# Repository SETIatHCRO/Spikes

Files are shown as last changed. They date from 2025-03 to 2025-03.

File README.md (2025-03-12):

## SPIKES - Spectrum Plotter and Interface Kit for EMI Scanning

SPIKES is a test setup to capture the emission profiles of potential RFI emitters at the Hat Creek Radio Observatory. 

The setup consists of a spectrum analyzer, a computer running the SPIKES application, an antenna and amplification system. 

The system is located in Lab 2 at HCRO, in this tutorial only local operation is covered. For more details on remote operation please refer to the documentation.

Measurement data should always be updated using git push to this repository (see Git_Push_Guide in the Documentation).

### Running the Application
To start the SPIKES application, log in to the Sonata account, navigate to the lower left side of the screen and click on the `SPIKES` icon:

SPIKES on Desktop

Or for the computationally adept run the following command in your terminal:

```bash
spikes
```

### Configuration

You can create a configuration file for the desired measurement or reuse an existing one. 

To access the configuration files, click on the `Configuration` icon on the lower left side of the screen:

Configuration Button

Again, for the experienced (or remote) user, the configuration files can be accessed directly from the terminal:

```bash
~/SPIKES/Configuration
```

Each configuration file contains the parameters to be sent to the spectrum analyzer, the parameters are loaded into the application and sent to the spectrum analyzer when the configuration is selected from the dropdown menu. 

If you edit or create a new configuration file, select RELOAD from the dropdown menu to update the current configuration files.

Note: there are two main modes of operation, `FAST` and `HIGH-RES`.

#### Example configuration (fast_track.yml):

FAST mode will perform a Max Hold measurement, this mode is useful to capture high-amplitude non-continous emissions like Wifi or Cellular.

In this example the spectrum analyzer will sweep from 300 MHz to 10 GHz with a resolution bandwidth of 500 kHz and a video bandwidth of 500 kHz. The attenuation is set to 10 dB to avoid damage to the spectrum analyzer (a strong signal is expected). The display will refresh every second and the integration time is set to 5 seconds. The total number of traces is set to 5.

This will result in a total measurement time of 25 seconds.

In this example the sweep time would be 45 milliseconds which will be displayed as soon as the configuration is loaded into the spectrum analyzer. This means that each trace will contain the max hold values of 111 sweeps. ($\frac{5 s}{0.045 s}$ = 111.1 = 111 sweeps) 

```yaml
sweep_points:       1001    # number of points
start_freq:         300e6   # Hz
stop_freq:          10e9    # Hz
res_bw:             500e3   # Hz
vid_bw:             500e3   # Hz
attenuation:        10      # dB
mode:               FAST    # Mode of operation: HIGH-RES or FAST
# mode specific parameters
display_refresh:    1       # seconds (int or float)
integration_time:   5       # seconds (integer)
total_traces:       5       # integer or "cont" for continuous operation
```

#### Example configuration (slow_coach.yml):

HIGH-RES mode will perform a clear sweep of the spectrum for every trace, this mode is useful to capture low-amplitude continuous emissions like clock signals or harmonics.

In this example the spectrum analyzer will sweep from 300 MHz to 6 GHz with a resolution bandwidth of 5 kHz and a video bandwidth of 5 kHz. The attenuation is set to 0 dB (a faint signal will be measured). The mode is set to HIGH-RES and the number of traces is set to 2.

The sweep time will be 264.233 seconds, which will result in a total measurement time of 9 minutes.

```yaml
sweep_points:   1001        # number of points
start_freq:     300e6       # Hz
stop_freq:      6e9         # Hz
res_bw:         5e3         # Hz
vid_bw:         5e3         # Hz
attenuation:    0           # dB 
mode:           HIGH-RES    # Mode of operation: HIGH-RES or FAST
# mode specific parameters
num_aver:       2           # number of traces
```

### Measurement Process
1. Select a configuration from the dropdown menu.
2. Click the Start button to begin the measurement.
3. The progress bar will update to show the measurement progress.
4. The Stop button can be used to stop the measurement at completion of the current trace.
5. The Save button will open a dialog to save the data to a file.

Please note that stopping a measurement will always wait on completion of the current trace, as the limitations of GPIB communications do not allow to reset the specturm analyzer during the sweep. 

It is still possible however to stop the measurement manually by pressing the ESC button on the spectrum analyzer to exit remote operation and setting the resolution bandwith very high to end the current measurement quickly (which will reestablish GPIB responsiveness of the spectrum analyzer). This will of course result in no data being captured.

### Measurement Data

To access the measurement data, click on the `Measurements` icon on the lower left side of the screen:

Measurements Button

Or for the terminal savvy:

```bash
~/SPIKES/Measurements
```

The folder structure is automatically created and organized as follows:

```
Measurements
├── date[YYYY-MM-DD]
│   ├── time[HHhMM]-[config_name]
│   │   ├── data
│   │   │   ├── config file[config_name].yml
│   │   │   └── trace_n.csv
|   |   ├── imgs_legend
|   |   |   ├── combined_trace.png
|   |   |   └── trace_n.png
|   |   └── imgs_nolegend
|   |       ├── combined_trace.png
|   |       └── trace_n.png
```

for example:

`Measurements/2025-01-01/12h00-fast_track/data/trace_1.csv`

### Setup Schematic

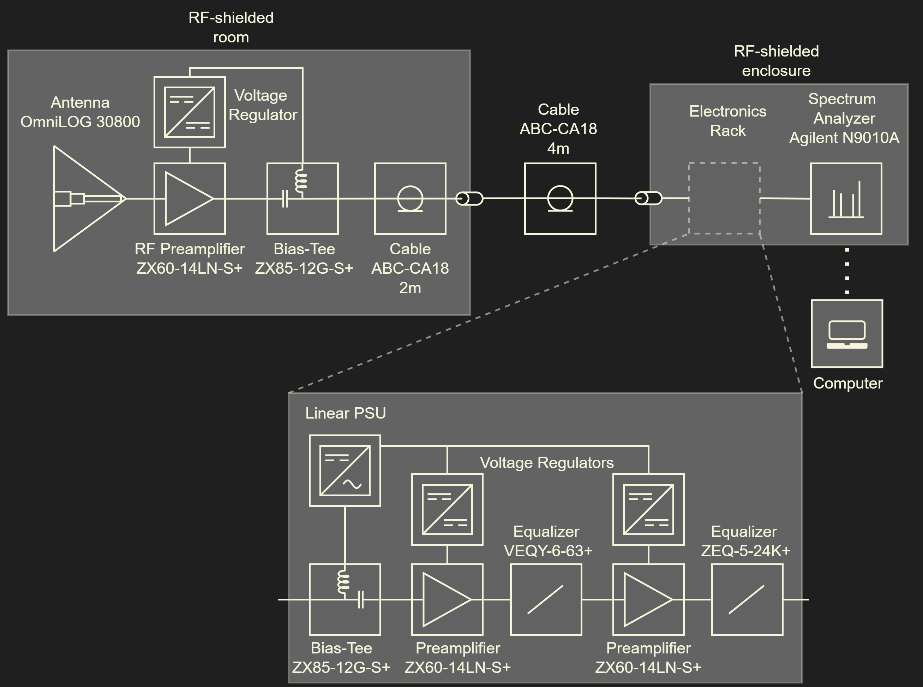
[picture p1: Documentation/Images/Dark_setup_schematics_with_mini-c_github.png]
Setup Schematic


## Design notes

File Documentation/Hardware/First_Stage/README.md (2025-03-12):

### First-Stage Amplifier Enclosure
This Enclosure is designed to house first-stage Mini-Circuits ZX60-14LN-S+ Amplifier, Bias-Tee and a Linear Voltage Regulator.

The Enclosure is designed to be mounted on a standard tripod mount, and has a 1/4" UNC thread on the bottom and back.

The Amplifier is powered via a 6V Linear Voltage Regulator, which has to be supplied by a 12V bias in the outgoing coaxial cable.

The Device was designed in Autodesk Inventor 2025, all necessary design files can be found in this directory.

The Enclosure is designed to be 3D printed, the step files in the directory are ready to print (however the current enclosures where printed with sla and sls processes and fdm is not yet tested).

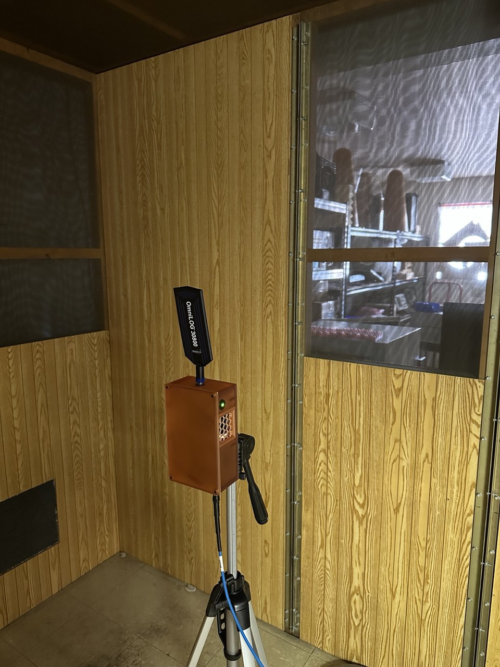
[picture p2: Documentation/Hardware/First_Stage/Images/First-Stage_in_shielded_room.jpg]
In Shielded Room

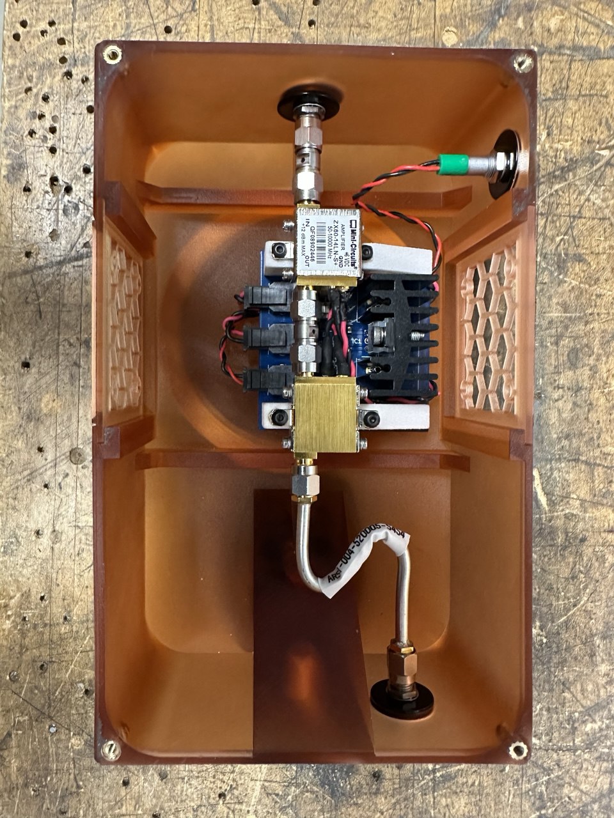
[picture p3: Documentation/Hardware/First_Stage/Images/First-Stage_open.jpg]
First Stage Open


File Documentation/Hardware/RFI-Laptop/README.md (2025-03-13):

### RFI-Laptop

Info about the dedicated Laptop for Spikes in Lab 2

#### General

  OS: Ubuntu 24.04 LTS

  Hostname: RFI-Laptop1.hcro.org

  Static-IP: 192.182.123.54

  BIOS-Settings: `Security -> I/O Port Access` Bluetooth: OFF, WiFi: OFF

#### Hardware

  Model: Lenovo ThinkPad E14 Gen 5 - 21JSS0Y500

  Processor: AMD Ryzen 7 7730U @ 2.00 GHz 1 Processor, 8 Cores, 16 Threads 

  Ram: 14.83 GB DDR4 SDRAM

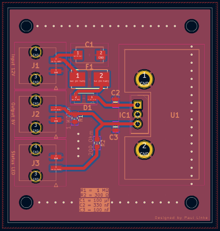
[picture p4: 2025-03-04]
Documentation/Hardware/Linear_Voltage_Regulator_6V/Images/Linear_Voltage_Regulator_Footprint.png

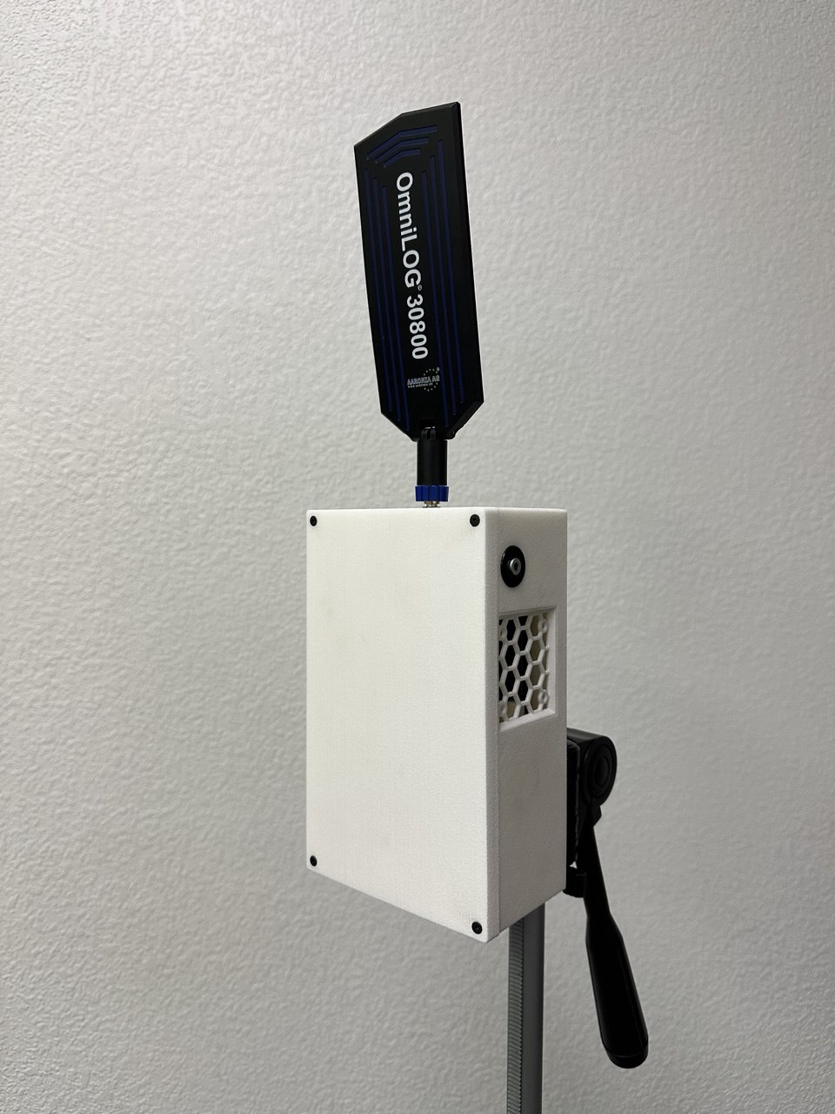
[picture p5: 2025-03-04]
Documentation/Hardware/First_Stage/Images/First-Stage_Nylon_Antenna.jpg

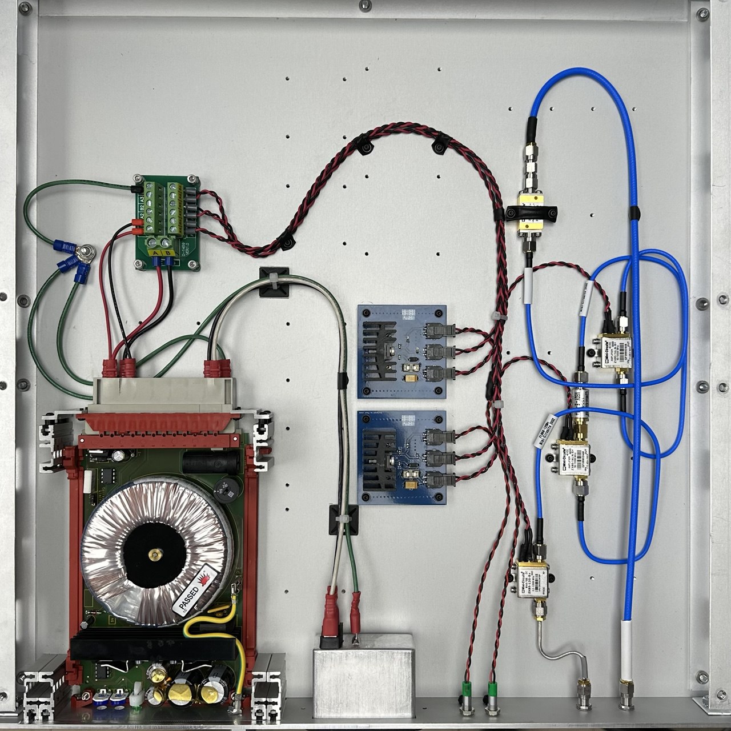
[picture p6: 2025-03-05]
Documentation/Hardware/Second_Stage/Images/Second_Stage_Top.jpg

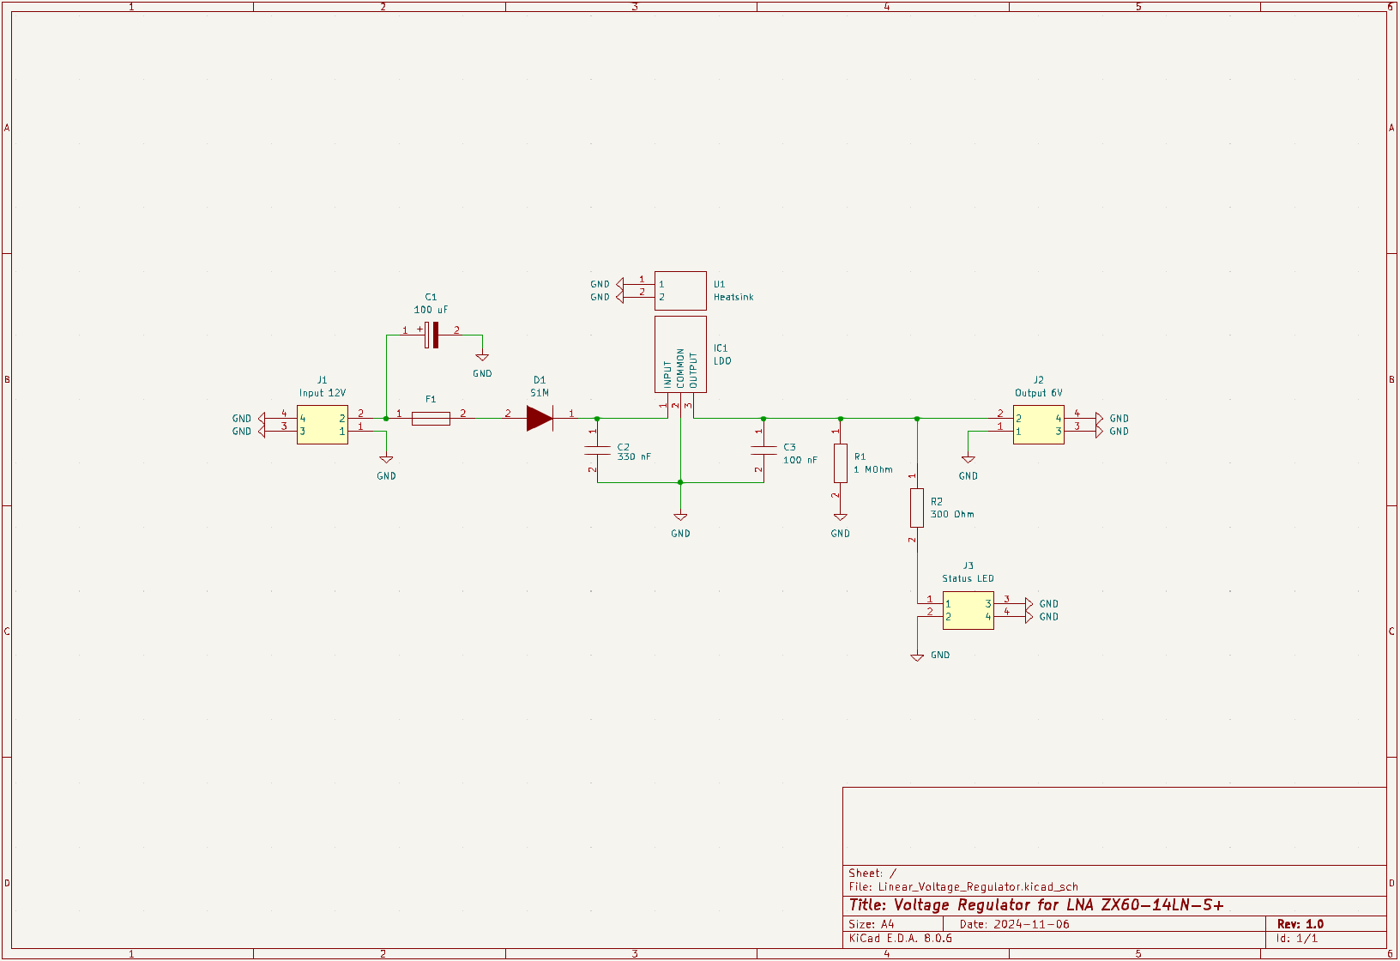
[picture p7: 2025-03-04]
Documentation/Hardware/Linear_Voltage_Regulator_6V/Images/Linear_Voltage_Regulator_Schematic.png

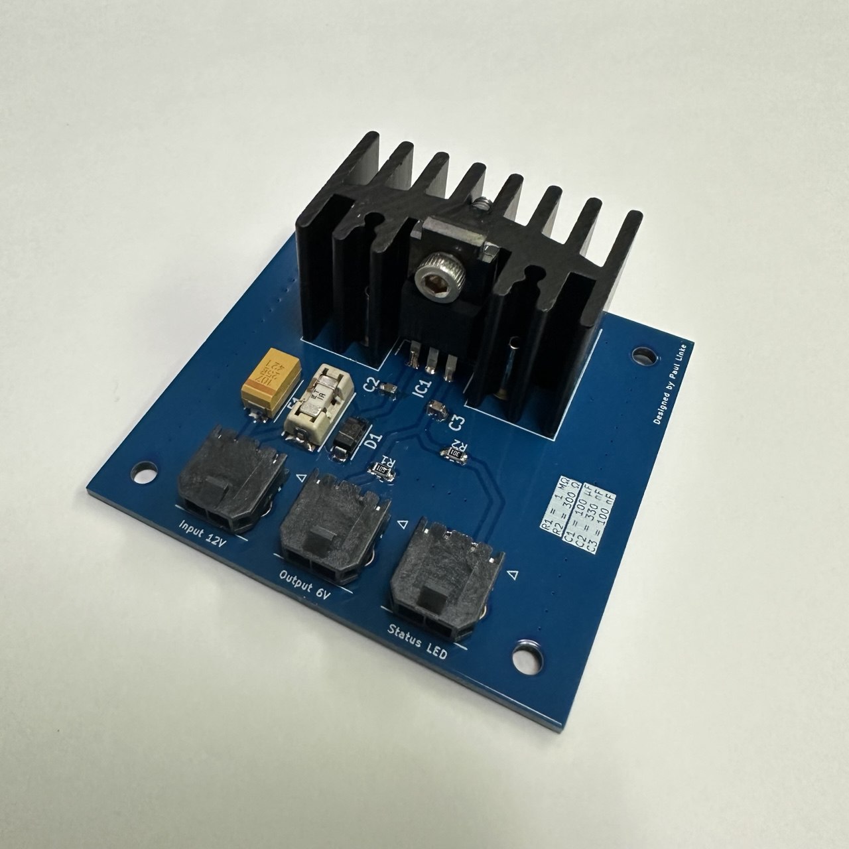
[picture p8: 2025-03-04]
Documentation/Hardware/Linear_Voltage_Regulator_6V/Images/Linear_Voltage_Regulator_real.png

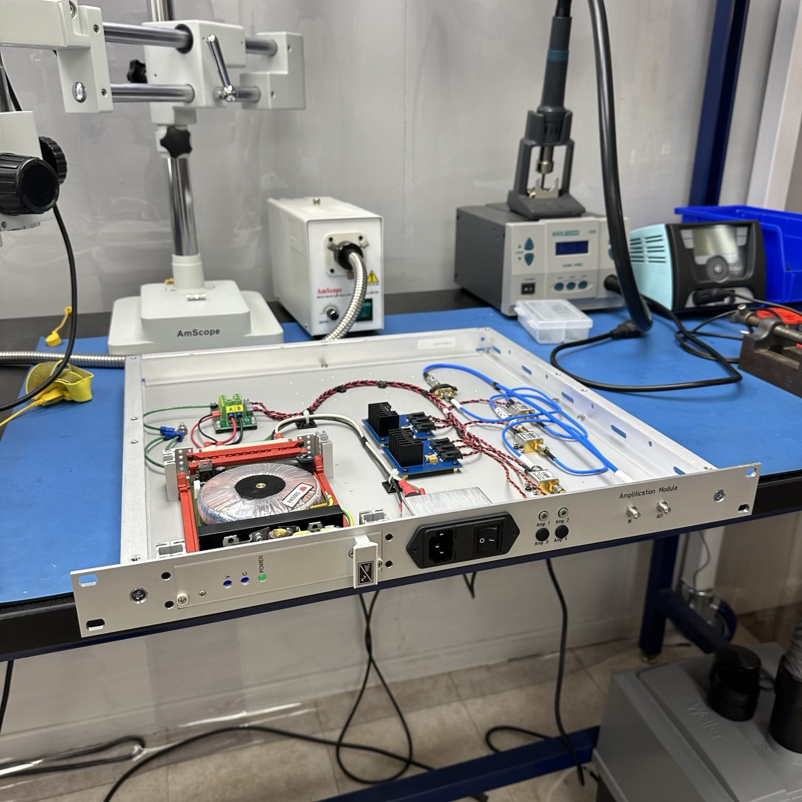
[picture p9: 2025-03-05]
Documentation/Hardware/Second_Stage/Images/Second_Stage_Front.jpg

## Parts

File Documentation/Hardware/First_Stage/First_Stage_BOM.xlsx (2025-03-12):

Sourcing List for SPIKES First Stage
QTY | Type | Name | Formfactor/Package | Manufacturer | Mfr. # | Link Vendor | Datasheet | Vendor
1 | Amplifier | ZX60-14LN-S+ | Mini-Circuits - GC957 | Mini-Circuits | ZX60-14LN-S+ | https://www.minicircuits.com/WebStore/dashboard.html?model=ZX60-14LN-S%2B | https://www.minicircuits.com/pdfs/ZX60-14LN-S+.pdf | Mini-Circuits
1 | Bias-Tee | ZX85-12G-S+ | Mini-Circuits - GC957 | Mini-Circuits | ZX85-12G-S+ | https://www.minicircuits.com/WebStore/dashboard.html?model=ZX85-12G-S%2B | https://www.minicircuits.com/pdfs/ZX85-12G-S+.pdf | Mini-Circuits
2 | SMA-Male2Male | SM-SM50+ | Mini-Circuits - DJ951 | Mini-Circuits | SM-SM50+ | https://www.minicircuits.com/WebStore/dashboard.html?model=SM-SM50%2B | https://www.minicircuits.com/pdfs/SM-SM50+.pdf | Mini-Circuits
2 | SMA-Passthrough | SM-SF50+ | Mini-Circuits - DJ952 | Mini-Circuits | SM-SF50+ | https://www.minicircuits.com/WebStore/dashboard.html?model=SF-SF50%2B | https://www.minicircuits.com/pdfs/SF-SF50+.pdf | Mini-Circuits
1 | LED | LED Green Panelmount | Panelmount, 6mm hole | Apem | Q6F3GXXG02E | https://www.mouser.com/ProductDetail/Apem/Q6F3GXXG02E?qs=4pzlT8jjbhczJGL6%2Fke6ug%3D%3D (https://www.minicircuits.com/WebStore/dashboard.html?model=ZX85-12G-S%2B) | https://www.mouser.com/datasheet/2/26/indicators_serie_Q6_-3359460.pdf | Mouser
1 | SMA-Male2Male | SMA-Cable 80mm | SMA-SMA Formable | Pasternak | PE3867LF-9CM | https://www.pasternack.com/showProduct.aspx?ProductID= | https://www.pasternack.com/images/ProductPDF/PE3867LF.pdf | Pasternak
1 | Threaded Insert | Ruthex - RX-M2.5x5.7 - 70 pcs | M2.5x5.7 | Ruthex | GE-M25x57-001 | https://www.amazon.com/ruthex-Threaded-Insert-Pieces-Ultrasound/dp/B088QJDPKK/ref=sr_1_3?sr=8-3 | https://www.ruthex.de/en/collections/gewindeeinsatze/products/ruthex-gewindeeinsatz-m2-5-70-stuck-rx-m2-5x5-7-messing-gewindebuchsen | Amazon
1 | Threaded Insert | Ruthex - RX-1/4" 20x12.7 - 20 pcs | 1/4"x12.7 | Ruthex | GE-1/4x127-001 | https://www.amazon.com/ruthex-Thread-Insert-20x12-7-Ultrasound/dp/B09MTS6ZZQ/ref=sr_1_3?sr=8-3 | https://www.ruthex.de/en/collections/gewindeeinsatze/products/ruthex-gewindeeinsatz-1-4-kameragewinde-20-stuck-rx-1-4-20x12-7-messing-gewindebuchsen-fur-3d-dr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 | Amazon
1 | Washers | M6 Washers | M6x1.3x17.7 | kvohlum | - | https://www.amazon.com/M6-Stainless-Washers-17-7mm-Diameter/dp/B0CX5GR7KG?cv_ct_cx=m7%2Bwasher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 | none | Amazon
1 | Standoffs | M2.5 Standoff Assortment Brass | M2.5 assortment | helifouner | - | https://www.amazon.com/HELIFOUNER-Standoffs-Assortment-Threaded-Motherboard/dp/B0B7SNCFF1?s=industrial&sp_csd=d2lkZ2V0TmFtZT1zcF9hdGY | none | Amazon
1 | Screws | M2.5 Screw Assortment Steel Countersunk | M2.5 assortment | Kindroufly | - | https://www.amazon.com/Kindroufly-Pieces-Countersunk-Washers-Assortment/dp/B0BLCG712G | none | Amazon
1 | Screws | M2.5 Screw Assortment Steel Button Head | M2.5 assortment | Kindroufly | - | https://www.amazon.com/Kindroufly-Pieces-Countersunk-Washers-Assortment/dp/B0BLCG5VS6 | none | Amazon
1 | 3d Print | First Stage Bottom |  | HCRO | First_Stage_BoxBottom.ipt |  |  | PCBWay
1 | 3d Print | First Stage Top |  | HCRO | First_Stage_BoxTop.ipt |  |  | PCBWay
1 | 3d Print | Voltage Regulator Bracket Left |  | HCRO | PCB-LNA.ipt |  |  | PCBWay
1 | 3d Print | Voltage Regulator Bracket Right |  | HCRO | PCB-LNA_MIR.ipt |  |  | PCBWay
2 | 3d Print | Hex-Grill |  | HCRO | First_Stage_HexGrill.ipt |  |  | PCBWay

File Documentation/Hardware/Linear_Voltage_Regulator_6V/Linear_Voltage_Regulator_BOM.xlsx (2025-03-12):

Sourcing List for 10x LDO_PSU PCB
QTY | Unit | Type | Name | Formfactor/Package | Manufacturer | Mfr. # | Link Vendor | Datasheet | Vendor | Cost p.P. $
10 | pcs | LDO | LDO 21V-6V1A TO-220 | TO-220 | Rohm | BA17806CP-E2 | ↗ (https://www.mouser.com/ProductDetail/ROHM-Semiconductor/BA17806CP-E2?qs=IsRgwgmxh6%252Bu7gXf8CL%252Bqw%3D%3D) | ↗ (https://www.mouser.com/ProductDetail/ROHM-Semiconductor/BA17806CP-E2?qs=IsRgwgmxh6%252Bu7gXf8CL%252Bqw%3D%3D) | Mouser | 1.87
10 | pcs | Tant Cap | Tantalum Capacitor 100uF | 2917 (7343 metric) | KEMET | T491X107K025AT | ↗ (https://www.mouser.com/ProductDetail/KEMET/T491X107K025AT?qs=QpHsZXO%252BQJ%252BKFgQiUckA6A%3D%3D) | ↗ (https://www.mouser.com/datasheet/2/447/KEM_T2005_T491-3316937.pdf) | Mouser | 2.57
10 | pcs | Cer Cap | Ceramic Capacitor 0.33uF | 0805 (2012 metric) | MuRata | GRM21AR72A334KAC5L | ↗ (https://www.mouser.com/ProductDetail/Murata-Electronics/GRM21AR72A334KAC5L?qs=vS1sKHMaE9WxhFYLmviwXA%3D%3D) | ↗ (https://www.mouser.com/datasheet/2/281/1/GRM21AR72A334KAC5_01A-1986692.pdf) | Mouser | 0.52
10 | pcs | Cer Cap | Ceramic Capacitor 0.1uF | 0805 (2012 metric) | MuRata | GCM21BR72A104KA37L | ↗ (https://www.mouser.com/ProductDetail/Murata-Electronics/GCM21BR72A104KA37L?qs=aEuGZpxfbxU57i7kalIPTw%3D%3D) | ↗ (https://www.mouser.com/datasheet/2/281/1/GCM21BR72A104KA37_01A-3145807.pdf) | Mouser | 0.13
10 | pcs | Resistor | 1 MOhm Thin Film Resistor | 0805 (2012 metric) | Panasonic | ERJ-U1TF2000U | ↗ (https://www.mouser.com/ProductDetail/Panasonic/ERA-6AEB105V?qs=2pXEX08Cf1VGLbL%252By9J2zw%3D%3D) | ↗ (https://www.mouser.com/datasheet/2/315/AOA0000C307-1149632.pdf) | Mouser | 0.14
10 | pcs | Resistor | 300 Ohm Thin Film Resistor | 0805 (2012 metric) | Panasonic | ERA-6AEB301V | ↗ (https://www.mouser.com/ProductDetail/Panasonic/ERA-6AEB301V?qs=m8myXnDJXpWgbmI3heQnEA%3D%3D) | ↗ (https://www.mouser.com/datasheet/2/315/AOA0000C307-1149632.pdf) | Mouser | 0.14
10 | pcs | Diode | Diode S1M 1000V 1A | DO-214AC | Onsemi | S1M | ↗ (https://www.mouser.com/ProductDetail/onsemi-Fairchild/S1M?qs=RJwZ8kJo1mhFujnIpzoJdg%3D%3D) | ↗ (https://www.mouser.com/datasheet/2/308/1/S1M_D-2320166.pdf) | Mouser | 0.22
10 | pcs | Fuse | Slow Blow Fuse and Holder assembly | 9.73 mm x 5.03 mm | Littelfuse | 0154001.DRT | ↗ (https://www.mouser.com/ProductDetail/Littelfuse/0154001.DRT?qs=gu7KAQ731UQPKHSDuMkClg%3D%3D) | ↗ (https://www.littelfuse.com/media?resourcetype=datasheets&itemid=63f61b85-5fc5-4f00-9ca9-8d59a6252d71) | Mouser | 2.88
30 | pcs | Connector | Molex Microfit 3.0 2-Position Terminal | Microfit 3.0 right angle | Molex | 43650-0211 | ↗ (https://www.mouser.com/ProductDetail/Molex/43650-0211?qs=z57USrEQgt0F0sS1hGS9Bw%3D%3D) | ↗ (https://www.molex.com/en-us/products/part-detail/436500211?display=pdf) | Mouser | 2.76
10 | pcs | Thermal Pad | Thermally conductive isolation Pad | TO-220 | Bergquist | 7403-09AC-67 | ↗ (https://www.mouser.com/ProductDetail/Bergquist-Company/7403-09AC-67?qs=Imq1NPwxi74BYsBpsah2Hw%3D%3D) | ↗ (https://www.mouser.com/datasheet/2/48/BERGQUIST_SIL_PAD_TSP_900_en_GL-3432587.pdf) | Mouser | 1.35
10 | pcs | LED | LED Green Panelmount | Panelmount, 6mm hole | Apem | Q6F3GXXG02E | ↗ (https://www.mouser.com/ProductDetail/Apem/Q6F3GXXG02E?qs=4pzlT8jjbhczJGL6%2Fke6ug%3D%3D) | ↗ (https://www.mouser.com/datasheet/2/26/indicators_serie_Q6_-3359460.pdf) | Mouser | 12.15
10 | pcs | Heatsink | TO-220 Heatsink | TO-220 | RS Pro | 263-251 | ↗ (https://www.distrelec.biz/en/heat-sink-17-9k-20x35x20mm-rs-pro-263251/p/30404202) | ↗ (https://media.distrelec.com/Web/Downloads/_t/ds/263251_eng_tds.pdf) | Distrelec | 1.60
10 | pcs | PCB | Linear Voltage Regulator PCB |  | HCRO |  |  |  | JLCPCB
 |  |  |  |  |  |  |  |  | Total Cost | 318.5 | $

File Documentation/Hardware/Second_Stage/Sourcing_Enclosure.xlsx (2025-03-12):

Sourcing Second Stage
QTY | Type | Name | Formfactor | Manufacturer | Mfr. # | Link | Datasheet | Vendor
1 | Rack Chassis | 19 Inch Rackmount Utility Chassis | 1U 19 Inch Unit | General Devices | CHA-1X17 | https://www.newark.com/general-devices/cha-1x17/utility-chassis-aluminum-rack/dp/97F3032 | https://www.farnell.com/datasheets/169855.pdf | Newark
1 | Bottom Plate | Custom Bottom Plate for Utility Chassis | 1U 19 Inch Unit | Front Panel Express | FrontPanel.fpd | - | - | Front Panel Express
1 | Front Plate | Custom Front Plate for Utility Chassis | 1U 19 Inch Unit | Front Panel Express | BottomPlate.fpd | - | - | Front Panel Express
1 | Linear PSU | AC/DC Linear Regulator | 3u 6hp depth: 172mm | Schroff | 13105-002 | https://schroff.nvent.com/en-us/products/enc13105-002 | https://schroff.nvent.com/sites/g/files/hdkjer281/files/acquiadam_assets/2021-11/73972-020_nV_.pdf?asset_type=Data%20Sheet | nvent
1 | PSU Front Panel | Front Panel for Schroff PSUs | 3u 6hp | Schroff | 21005-475 | https://www.nvent.com/en-us/schroff/products/enc21005-475 | https://www.nvent.com/sites/default/files/acquiadam_assets/2021-06/73972-043.pdf | nvent
1 | PSU Coding Strip | Coding Strip for Schroff PSUs | - | Schroff | 60800-123 | https://www.nvent.com/en-us/schroff/products/enc60800-123 | none | nvent
1 | PSU Connector | Back Connector for Schroff PSUs | - | Schroff | 69001-733 | https://www.nvent.com/en-us/schroff/products/enc69001-733 | https://www.nvent.com/sites/default/files/acquiadam_assets/2021-06/connectors.pdf | nvent
1 | Power Inlet | Compact filtered power entry module | - | Schaffner | FN281-1-06 | https://www.digikey.com/en/products/detail/schaffner-emc-inc/FN281-1-06/1997102?gad_source=1 | https://www.schaffner.com/product/FN280/Schaffner_datasheet_FN280.pdf | digikey
1 | Equalizer | ZEQ-5-24K+ | Mini-Circuits - RA2937 | Mini-Circuits | ZEQ-5-24K+ | https://www.minicircuits.com/WebStore/dashboard.html?model=ZEQ-5-24K%2B | https://www.minicircuits.com/pdfs/ZEQ-5-24K+.pdf | Mini-Circuits
1 | Equalizer | VEQY-6-63+ | Mini-Circuits - FF704 | Mini-Circuits | VEQY-6-63+ | https://www.minicircuits.com/WebStore/dashboard.html?model=VEQY-6-63%2B | https://www.minicircuits.com/pdfs/VEQY-6-63+.pdf | Mini-Circuits
2 | Amplifier | ZX60-14LN-S+ | Mini-Circuits - GC957 | Mini-Circuits | ZX60-14LN-S+ | https://www.minicircuits.com/WebStore/dashboard.html?model=ZX60-14LN-S%2B | https://www.minicircuits.com/pdfs/ZX60-14LN-S+.pdf | Mini-Circuits
1 | Bias-Tee | ZX85-12G-S+ | Mini-Circuits - GC957 | Mini-Circuits | ZX85-12G-S+ | https://www.minicircuits.com/WebStore/dashboard.html?model=ZX85-12G-S%2B | https://www.minicircuits.com/pdfs/ZX85-12G-S+.pdf | Mini-Circuits
2 | SMA-Passthrough | SM-SF50+ | Mini-Circuits - DJ952 | Mini-Circuits | SM-SF50+ | https://www.minicircuits.com/WebStore/dashboard.html?model=SF-SF50%2B | https://www.minicircuits.com/pdfs/SF-SF50+.pdf | Mini-Circuits
2 | LED | LED Green Panelmount | Panelmount, 6mm hole | Apem | Q6F3GXXG02E | https://www.mouser.com/ProductDetail/Apem/Q6F3GXXG02E?qs=4pzlT8jjbhczJGL6%2Fke6ug%3D%3D (https://www.minicircuits.com/WebStore/dashboard.html?model=ZX85-12G-S%2B) | https://www.mouser.com/datasheet/2/26/indicators_serie_Q6_-3359460.pdf | Mouser
1 | Standoffs | M2.5 Standoff Assortment Brass | M2.5 assortment | helifouner | - | https://www.amazon.com/HELIFOUNER-Standoffs-Assortment-Threaded-Motherboard/dp/B0B7SNCFF1?s=industrial&sp_csd=d2lkZ2V0TmFtZT1zcF9hdGY | none | Amazon
1 | Screws | M2.5 Screw Assortment Steel Button Head | M2.5 assortment | Kindroufly | - | https://www.amazon.com/Kindroufly-Pieces-Countersunk-Washers-Assortment/dp/B0BLCG5VS6 | none | Amazon
1 | Distribution Module | 30Amp 48V 2x6 Position Terminal | PCB | Oono | - | https://www.amazon.com/dp/B09D3BV22M | none | Amazon
2 | Voltage Regulator | Linear Voltage Regulator | PCB | HCRO | - | https://github.com/SETIatHCRO/Spikes/tree/main/Documentation/Hardware/Linear_Voltage_Regulator_6V | none | none

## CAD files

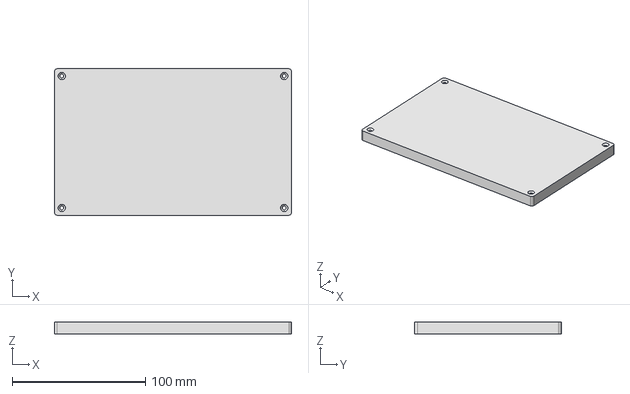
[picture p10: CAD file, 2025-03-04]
Documentation/Hardware/First_Stage/STEP-FILES/First_Stage_Top_Print.stp
178.0 x 110.1 x 9.00 mm

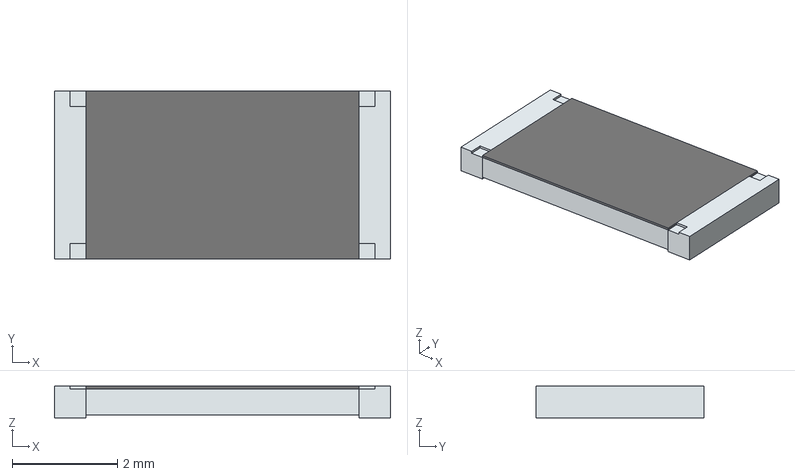
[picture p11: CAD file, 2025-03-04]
Documentation/Hardware/Linear_Voltage_Regulator_6V/Components_3d_footprints/LIB_200Ohm_ThickFilm_SMD/ERJ-U1TF2000U/3D/ERJ-U1TF2000U.stp
6.40 x 3.20 x 0.6 mm
solidBody
Terminal
solidTop

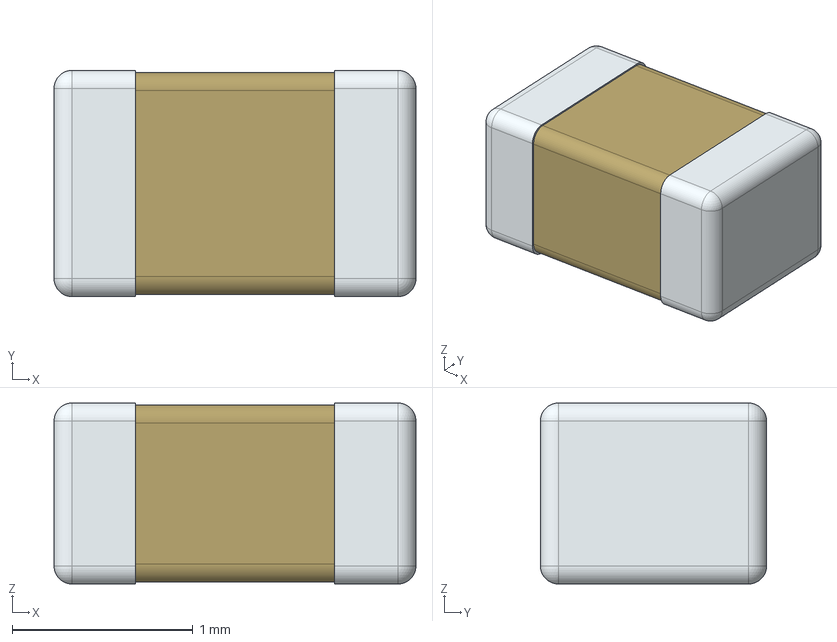
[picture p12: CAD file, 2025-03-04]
Documentation/Hardware/Linear_Voltage_Regulator_6V/Components_3d_footprints/LIB_CerCap_330nF_muRata/GRM21AR72A334KAC5L/3D/GRM21AR72A334KAC5L.stp
2.00 x 1.25 x 1.00 mm

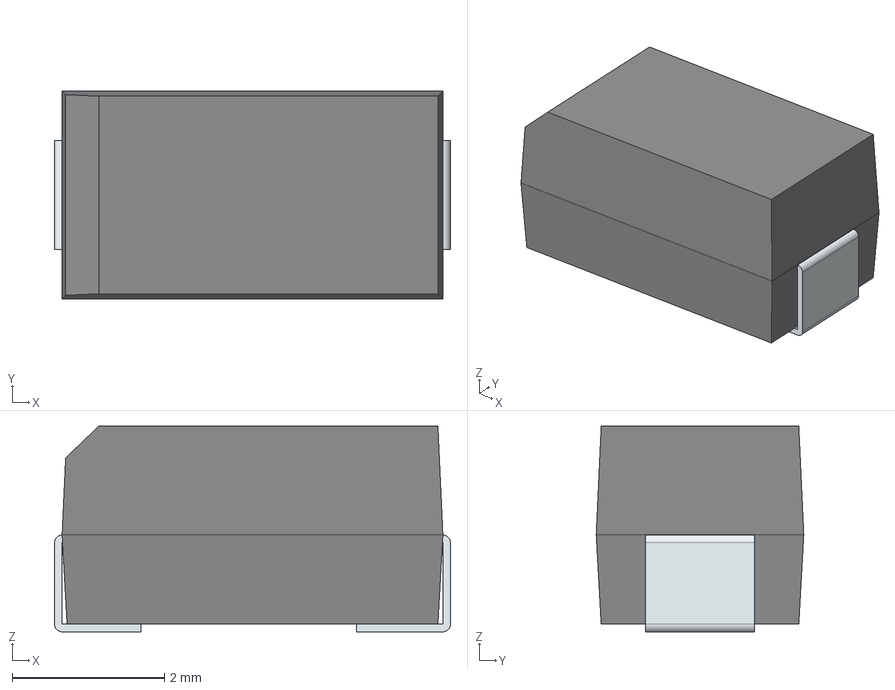
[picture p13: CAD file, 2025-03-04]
Documentation/Hardware/Linear_Voltage_Regulator_6V/Components_3d_footprints/LIB_Diode_1000V_1A_S1M/S1M/3D/S1M.stp
5.20 x 2.73 x 2.70 mm
FilletPin1
FilletPin2

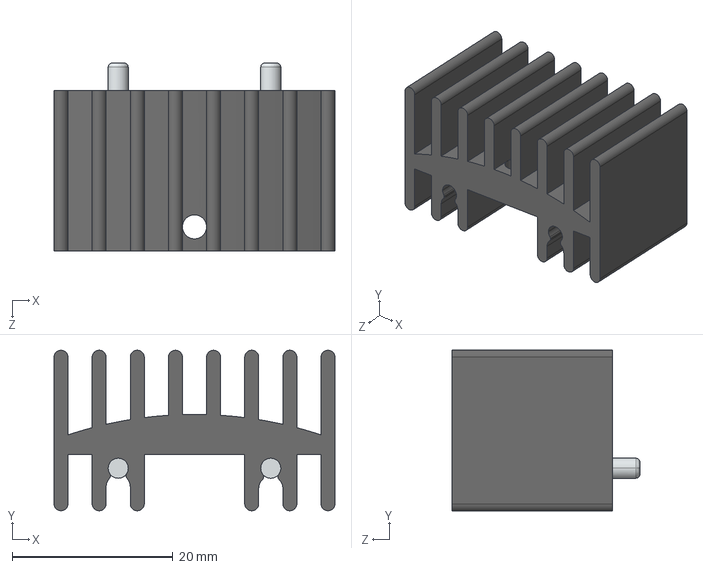
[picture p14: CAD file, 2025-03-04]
Documentation/Hardware/Linear_Voltage_Regulator_6V/Components_3d_footprints/LIB_HeatsinkTO-220_RSPRO/Heatsink_RSPRO-263-251.step
35.0 x 20.0 x 23.4 mm

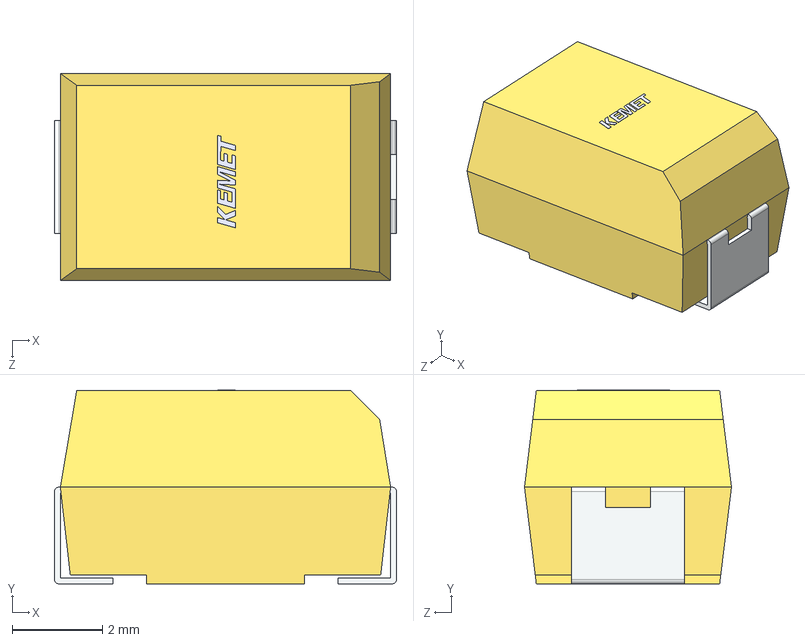
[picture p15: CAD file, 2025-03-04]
Documentation/Hardware/Linear_Voltage_Regulator_6V/Components_3d_footprints/LIB_TantalumCap_100uF_KEMET/T491X107K025AT/3D/T491X107K025AT.stp
7.60 x 4.31 x 4.60 mm

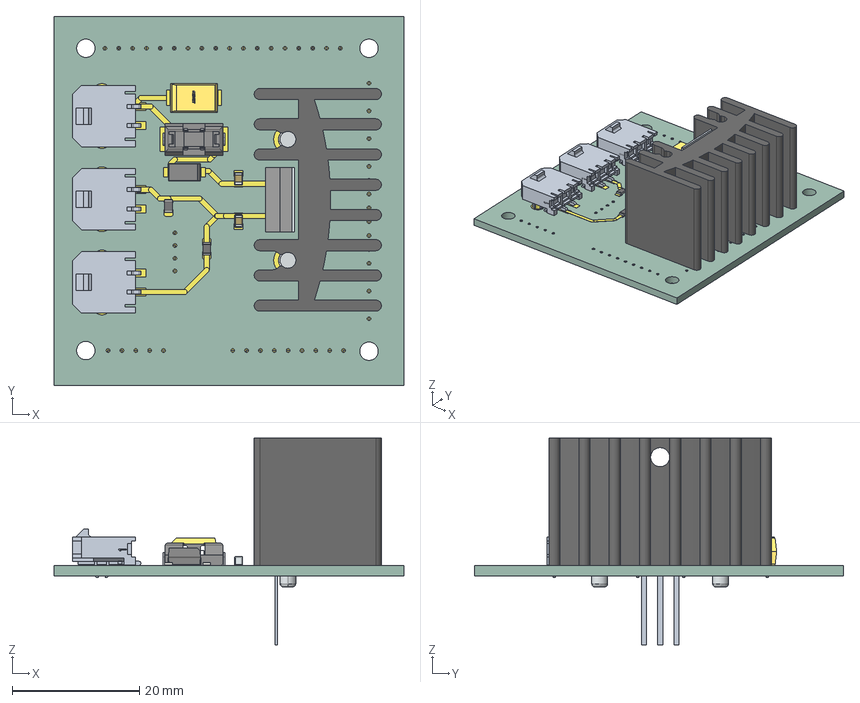
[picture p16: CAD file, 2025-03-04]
Documentation/Hardware/Linear_Voltage_Regulator_6V/Linear_Voltage_Regulator.step
55.0 x 58.0 x 32.5 mm
ASSEMBLY x 4
CTSM_TCM2NK_7343_L7.6W4.6H4.3T0.13S1.3F2.5A3.6B0.65E3.5G3.5P1.7R1X0.2
0154010.DR
R_0805_2012Metric x 2
5595D9A1-7FEB-42A4-8036-384FF62542EF
Voltage_Regulator_for_ZX60-14LN-S+_track_1
Voltage_Regulator_for_ZX60-14LN-S+_track_2
Voltage_Regulator_for_ZX60-14LN-S+_track_3
Voltage_Regulator_for_ZX60-14LN-S+_track_4
Voltage_Regulator_for_ZX60-14LN-S+_track_5
Voltage_Regulator_for_ZX60-14LN-S+_track_6
Voltage_Regulator_for_ZX60-14LN-S+_track_7
Voltage_Regulator_for_ZX60-14LN-S+_track_8
Voltage_Regulator_for_ZX60-14LN-S+_track_9
Voltage_Regulator_for_ZX60-14LN-S+_track_10
Voltage_Regulator_for_ZX60-14LN-S+_track_11
Voltage_Regulator_for_ZX60-14LN-S+_track_12
Voltage_Regulator_for_ZX60-14LN-S+_track_13
Voltage_Regulator_for_ZX60-14LN-S+_track_14
Voltage_Regulator_for_ZX60-14LN-S+_track_15
Voltage_Regulator_for_ZX60-14LN-S+_track_16
Voltage_Regulator_for_ZX60-14LN-S+_track_17
Voltage_Regulator_for_ZX60-14LN-S+_track_18
Voltage_Regulator_for_ZX60-14LN-S+_track_19
Voltage_Regulator_for_ZX60-14LN-S+_track_20
Voltage_Regulator_for_ZX60-14LN-S+_track_21
Voltage_Regulator_for_ZX60-14LN-S+_track_22
Voltage_Regulator_for_ZX60-14LN-S+_track_23
Voltage_Regulator_for_ZX60-14LN-S+_track_24
Voltage_Regulator_for_ZX60-14LN-S+_track_25
Voltage_Regulator_for_ZX60-14LN-S+_track_26
Voltage_Regulator_for_ZX60-14LN-S+_track_27
Voltage_Regulator_for_ZX60-14LN-S+_track_28
Voltage_Regulator_for_ZX60-14LN-S+_track_29
Voltage_Regulator_for_ZX60-14LN-S+_track_30
Voltage_Regulator_for_ZX60-14LN-S+_track_31
Voltage_Regulator_for_ZX60-14LN-S+_track_32
Voltage_Regulator_for_ZX60-14LN-S+_track_33
Voltage_Regulator_for_ZX60-14LN-S+_pad_1
Voltage_Regulator_for_ZX60-14LN-S+_pad_2
Voltage_Regulator_for_ZX60-14LN-S+_pad_3
Voltage_Regulator_for_ZX60-14LN-S+_pad_4
Voltage_Regulator_for_ZX60-14LN-S+_pad_5
Voltage_Regulator_for_ZX60-14LN-S+_pad_6
Voltage_Regulator_for_ZX60-14LN-S+_pad_7
Voltage_Regulator_for_ZX60-14LN-S+_pad_8
Voltage_Regulator_for_ZX60-14LN-S+_pad_9
Voltage_Regulator_for_ZX60-14LN-S+_pad_10
Voltage_Regulator_for_ZX60-14LN-S+_pad_11
Voltage_Regulator_for_ZX60-14LN-S+_pad_12
Voltage_Regulator_for_ZX60-14LN-S+_pad_13
Voltage_Regulator_for_ZX60-14LN-S+_pad_14
Voltage_Regulator_for_ZX60-14LN-S+_pad_15
Voltage_Regulator_for_ZX60-14LN-S+_pad_16
Voltage_Regulator_for_ZX60-14LN-S+_pad_17
Voltage_Regulator_for_ZX60-14LN-S+_pad_18
Voltage_Regulator_for_ZX60-14LN-S+_pad_19
Voltage_Regulator_for_ZX60-14LN-S+_pad_20
Voltage_Regulator_for_ZX60-14LN-S+_pad_21
Voltage_Regulator_for_ZX60-14LN-S+_pad_22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

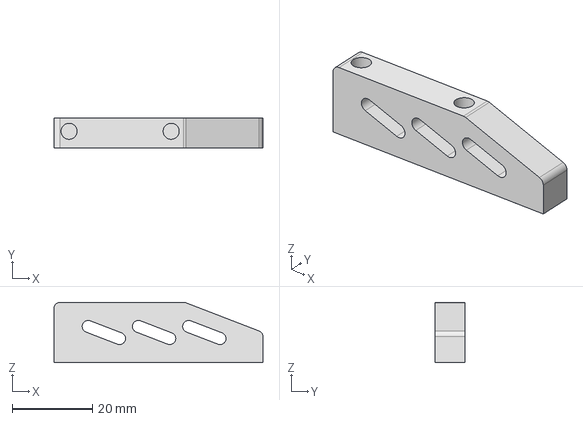
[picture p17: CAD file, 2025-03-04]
Documentation/Hardware/First_Stage/STEP-FILES/Regulator_Bracket_Left_Print.stp
52.0 x 7.50 x 15.0 mm

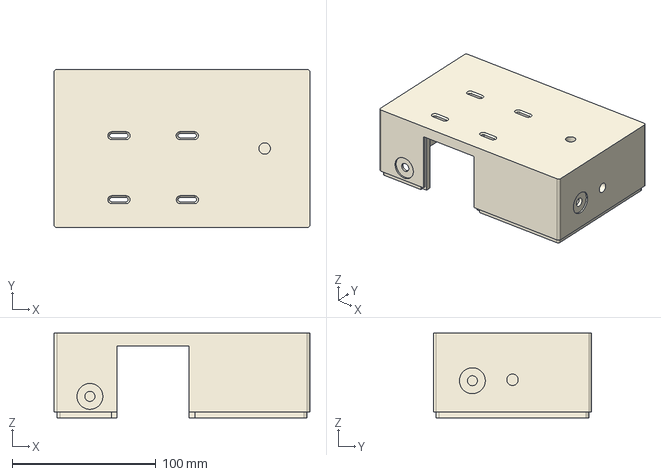
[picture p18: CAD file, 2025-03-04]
Documentation/Hardware/First_Stage/STEP-FILES/First_Stage_Bottom_Print.stp
178.0 x 110.1 x 59.0 mm

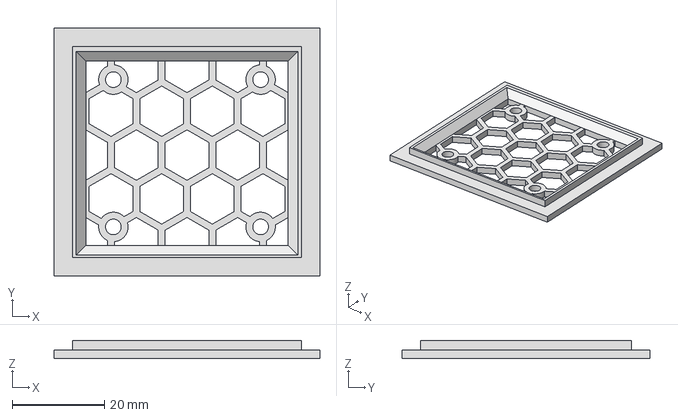
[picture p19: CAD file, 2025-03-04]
Documentation/Hardware/First_Stage/STEP-FILES/First_Stage_HexGrill_Print.stp
57.8 x 53.9 x 4.00 mm

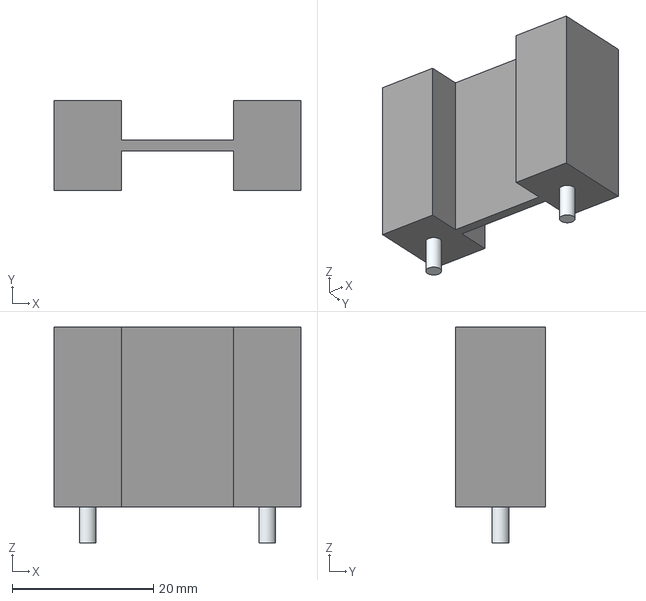
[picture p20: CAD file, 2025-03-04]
Documentation/Hardware/Linear_Voltage_Regulator_6V/Components_3d_footprints/LIB_HeatsinkTO-220_Aavid/513002B02500G/3D/513002B02500G.stp
34.9 x 12.7 x 30.5 mm
Leads x 2

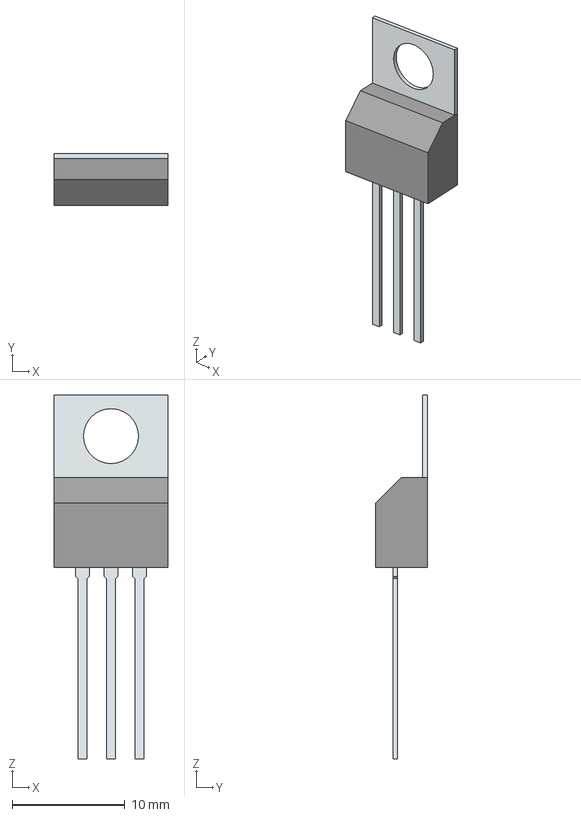
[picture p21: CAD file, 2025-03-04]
Documentation/Hardware/Linear_Voltage_Regulator_6V/Components_3d_footprints/LIB_LDO_21V-6V_Rohm/BA17806CP-E2/3D/BA17806CP-E2.stp
10.1 x 4.60 x 32.3 mm
Tab
PinsArray

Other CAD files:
Documentation/Hardware/Second_Stage/Drawings/BasePlate.dwg
Documentation/Hardware/Second_Stage/Drawings/FrontPanel.dwg
Documentation/Hardware/First_Stage/STEP-FILES/Regulator_Bracket_Right_Print.stp
Documentation/Hardware/First_Stage/First_Stage_BoxBottom.ipt
Documentation/Hardware/First_Stage/First_Stage_BoxTop.ipt
Documentation/Hardware/First_Stage/First_Stage_HexGrill.ipt
Documentation/Hardware/First_Stage/First_Stage_SPIKES.iam
Documentation/Hardware/First_Stage/OldVersions/First_Stage_BoxTop.0010.ipt
Documentation/Hardware/First_Stage/OldVersions/First_Stage_HexGrill.0017.ipt
Documentation/Hardware/First_Stage/OldVersions/First_Stage_SPIKES.0062.iam
Documentation/Hardware/First_Stage/OldVersions/PCB-LNA_MIR.0004.ipt
Documentation/Hardware/First_Stage/PCB-LNA.ipt
Documentation/Hardware/First_Stage/PCB-LNA_MIR.ipt
Documentation/Hardware/First_Stage/Parts/Hex_standoff_M2.5_10mm.ipt
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

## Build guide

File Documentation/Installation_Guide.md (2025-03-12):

## Installation Guide
### Abstract

This guide walks through the necessary steps to install the SPIKES application on a local machine. It allows the user to run the application on their own machine given the correct dependencies are installed.

This Guide is tested on Windows 11 and Ubuntu 24.04 LTS.

### Requirements
- Git (make sure it is up to date)
- Python 3.13
- Virtual environment

### Setup

1. Open a terminal and navigate to the directory where you want to install the application

    Linux, OSX:
    ```bash
    cd ~/path/to/directory
    ```

    Windows (using PowerShell):
    ```bash
    chdir C:\path\to\directory
    ```

2. Clone the repository
    
    if you have an SSH key set up with GitHub, you can clone the repository using SSH:
    ```bash
    git clone git@github.com:SETIatHCRO/Spikes.git
    ```
    
    else you can clone the repository using HTTPS:
    ```bash
    git clone https://github.com/SETIatHCRO/Spikes.git
    ```

    and navigate into the SPIKES directory
   
    Linux, OSX:
    ```bash
    cd Spikes
    ```

    Windows:
    ```bash
    chdir Spikes
    ```

3. Create the needed virtual environment
   
    Linux, OSX:
    ```bash
    python3.13 -m venv .venv
    ```

    Windows (to make sure you are using the correct version of python):

    ```bash 
    C:\path\to\python3.13 -m venv .venv
    # this should be: 
    # C:\Users\YourUsername\AppData\Local\Programs\Python\Python313\python.exe
    # or
    # C:\Program Files\Python313\python.exe for system-wide installations
    ```
  
    and activate it

    Linux, OSX:
    ```bash
    source .venv/bin/activate
    ```

    Windows:

    ```bash
    .venv\Scripts\Activate
    ```

4. Upgrade pip
   
    Linux, OSX:
    ```bash
    pip install --upgrade pip
    ```

    Windows:
    ```bash
    python.exe -m pip install --upgrade pip
    ```

    and install requirements
    
    ```bash
    pip install -r requirements.txt
    ```

5. Deactivate the virtual environment
   
    ```bash
    deactivate
    ```

6. The Application can now be started:

    Linux, OSX
    ```bash
    path/to/Cloned_Directory/.venv/bin/python3.13 path/to/Cloned_Directory/Application/main.py
    ```

    Windows
    ```bash
    path\to\Cloned_Directory\.venv\scripts\python.exe path\to\Cloned_Directory\Application\main.py

Note: there are countless ways of creating bash scripts, desktop links and start menu shortcuts to ease access to the app on all operating systems, please choose for yourself if and how you want to implement these.

#### One useful example for making a globally accessible command by creating a bash script (Linux, OSX):

1. In any directory (the file will be moved later), create a file called `shortcut.sh`:

    ```bash
    touch shortcut.sh
    ```

2. Open the file in a text editor:

    ```bash
    nano shortcut.sh
    ```

3. Add the previously used command to start the application (edit to match your paths):

    ```bash
    ### GNU nano x.x ############### shortcut.sh ########
    path/to/Cloned_Directory/.venv/bin/python3.13 path/to/Cloned_Directory/Application/main.py
    ```

    do not forget to save before exiting.

4. Make the file executable:

    ```bash
    chmod +x shortcut.sh
    ```

5. Move the file to a directory that is in your PATH (this will likely require sudo rights):

    ```bash
    sudo mv shortcut.sh /usr/local/bin/spikes
    ```

    /usr/local/bin/*spikes* 
    
    *spikes* will be the command to start the application, you can use whatever name you like here. 

6. You can now start the application from any directory:

    ```bash
    spikes
    ```

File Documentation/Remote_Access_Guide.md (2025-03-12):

## Remote Access Guide
### Abstract

This guide walks through the necessary steps to access the lab computer running the SPIKES application via SSH. It allows the user to access the lab computer from within the local network of HCRO or from outside the network via VPN.

Note: This method is absolutely viable to perform measurements and browse the data, however, it is easier and an overall more enjoyable experience to use the SPIKES application on the local machine. 

### Running SPIKES

The first step is connecting to the computer, if you are on windows, activate WSL (Windows Subsystem for Linux) and use install a linux distribution of your choice via the microsoft store (you will have a command line interface ready after installing and creating a user). 

If you are on linux or mac open a terminal and type the following command:

```bash
ssh -Y sonata@rfi-laptop1
# Be sure to use -Y for the GUI to work properly
```

After entering the password you will be connected to the computer. You can now run the application by typing the following command:

```bash
spikes
```

### Browsing the Measurements

In order to browse the measurements you will navigate to the Measurements directory thusly:

```bash
cd ~/SPIKES/Measurements
```

As described in the SPIKES README file, the folder structure is organized as follows:

```Folder Structure
Measurements
├── date[YYYY-MM-DD]
│   ├── time[HHhMM]-[config_name]
│   │   ├── data
│   │   │   ├── config file[config_name].yml
│   │   │   └── trace_n.csv
|   |   ├── imgs_legend
|   |   |   ├── combined_trace.png
|   |   |   └── trace_n.png
|   |   └── imgs_nolegend
|   |       ├── combined_trace.png
|   |       └── trace_n.png
```

To get measurement data from the lab computer to your local machine you can use the scp (Secure Copy) command:

```bash
scp -r user@address:/path/to/remote/directory /path/to/local/destination
# Using -r to copy directories, not necessary for single files
```

Example:

```bash
scp -r sonata@rfi-laptop1.hcro.org: ~/SPIKES/Measurements /home/YourUserName/Somewhere
# This will copy the whole Measurements directory to Somewhere on your local machine
```

### Creating a new Configuration

To create a new configuration you will navigate to the Configuration directory:

```bash
cd ~/SPIKES/Configuration
```

Here you will find the configuration files for the SPIKES application. To create a new configuration you can copy an existing configuration file and modify it to your needs:

```bash
cp fast_template.yml my_splendid_config.yml
```

You can now edit the configuration file with your favorite text editor (for example nano):

```bash
nano my_splendid_config.yml
```

You will be rewarded with the following sight:

```yaml
### GNU nano x.x ############### my_splendid_config.yml ########
sweep_points:     1001      # number of points
start_freq:       300e6     # Hz
stop_freq:        10e9      # Hz
res_bw:           500e3     # Hz
vid_bw:           500e3     # Hz
attenuation:      10        # dB
mode:             FAST      # Mode of operation: HIGH-RES or FAST
# mode specific parameters
display_refresh:  1         # seconds (int or float)
integration_time: 5         # seconds (integer)
total_traces:     5         # integer or "cont" for continuous operation
```

After saving the edited file the configuration is ready to be used within the SPIKES application.

Please refer to the Git_Push_Guide for a reminder to always push your changes to the repository.

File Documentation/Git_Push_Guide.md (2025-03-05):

## Git Push Guide
### Abstract

This guide serves as a reminder to push measurements and any changes made to configurations or code to this repository. 

This is much the most convenient way to have the measurement data available at any time.

### Pushing to GitHub

Suppose you have made some enlightening measurements using the lab computer and want to push them to the repository.

Note: this will work just the same when ssh'd into the lab computer.  (refer to the Remote Access Guide for more information)

1. Open a terminal and navigate to the SPIKES directory:

```bash
cd ~/SPIKES
```

2. Pull the latest changes from the repository:

It is always possible some changes have been made to the repository since the last time you pulled. To avoid conflicts it is best to pull the latest changes before pushing.

```bash
git pull
```

3. Add the changes to the staging area:

This command will add all changes to the staging area. If you only want to add specific files you can replace the `.` with the file name.

```bash
git add .
```

4. Commit the changes:

This command will commit the changes to the local repository. The `-m` flag is used to add a (required) message to the commit.

```bash
git commit -m "Message describing the changes made"
```

5. Push the changes to the repository:

This command will push the changes to the repository. On the Lab computer you will not be required to enter your username and password every time you push.

```bash
git push
```

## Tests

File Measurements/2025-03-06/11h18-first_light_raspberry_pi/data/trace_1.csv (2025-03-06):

5.000000000000000000e+08 | -7.600904846191410513e+01
5.115000000000000000e+08 | -7.598305511474609375e+01
5.230000000000000000e+08 | -7.634867095947269888e+01
5.345000000000000000e+08 | -7.670806121826170454e+01
5.460000000000000000e+08 | -7.653369903564450283e+01
5.575000000000000000e+08 | -7.640489196777339487e+01
5.690000000000000000e+08 | -7.678604125976559658e+01
5.805000000000000000e+08 | -7.627907562255859375e+01
5.920000000000000000e+08 | -7.651382446289059658e+01
6.035000000000000000e+08 | -7.561322021484380684e+01
6.150000000000000000e+08 | -7.567907714843750000e+01
6.265000000000000000e+08 | -7.516632843017579546e+01
6.380000000000000000e+08 | -7.449221038818359375e+01
6.495000000000000000e+08 | -7.449308013916019888e+01
6.610000000000000000e+08 | -7.436847686767579546e+01
6.725000000000000000e+08 | -7.429196929931640625e+01
6.840000000000000000e+08 | -7.402703094482420454e+01
6.955000000000000000e+08 | -7.408383941650390625e+01
7.070000000000000000e+08 | -7.353964233398440342e+01
7.185000000000000000e+08 | -7.384817504882809658e+01
7.300000000000000000e+08 | -7.396008300781250000e+01
7.415000000000000000e+08 | -7.445586395263670454e+01
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

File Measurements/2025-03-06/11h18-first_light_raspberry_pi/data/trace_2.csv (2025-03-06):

5.000000000000000000e+08 | -9.982772827148440342e+01
5.115000000000000000e+08 | -9.997933197021480112e+01
5.230000000000000000e+08 | -9.998643493652339487e+01
5.345000000000000000e+08 | -1.000351715087890057e+02
5.460000000000000000e+08 | -9.983216094970700283e+01
5.575000000000000000e+08 | -9.940048217773440342e+01
5.690000000000000000e+08 | -1.004887771606450002e+02
5.805000000000000000e+08 | -1.003415298461909941e+02
5.920000000000000000e+08 | -1.005911331176759944e+02
6.035000000000000000e+08 | -1.003727874755859943e+02
6.150000000000000000e+08 | -9.997491455078130684e+01
6.265000000000000000e+08 | -1.005580902099609943e+02
6.380000000000000000e+08 | -1.004811859130859943e+02
6.495000000000000000e+08 | -1.006703872680659941e+02
6.610000000000000000e+08 | -9.988711547851559658e+01
6.725000000000000000e+08 | -1.001218185424799998e+02
6.840000000000000000e+08 | -1.003585815429690058e+02
6.955000000000000000e+08 | -1.000415496826170028e+02
7.070000000000000000e+08 | -1.000130615234379974e+02
7.185000000000000000e+08 | -9.997840118408200283e+01
7.300000000000000000e+08 | -1.001526641845699999e+02
7.415000000000000000e+08 | -1.001179275512700002e+02
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

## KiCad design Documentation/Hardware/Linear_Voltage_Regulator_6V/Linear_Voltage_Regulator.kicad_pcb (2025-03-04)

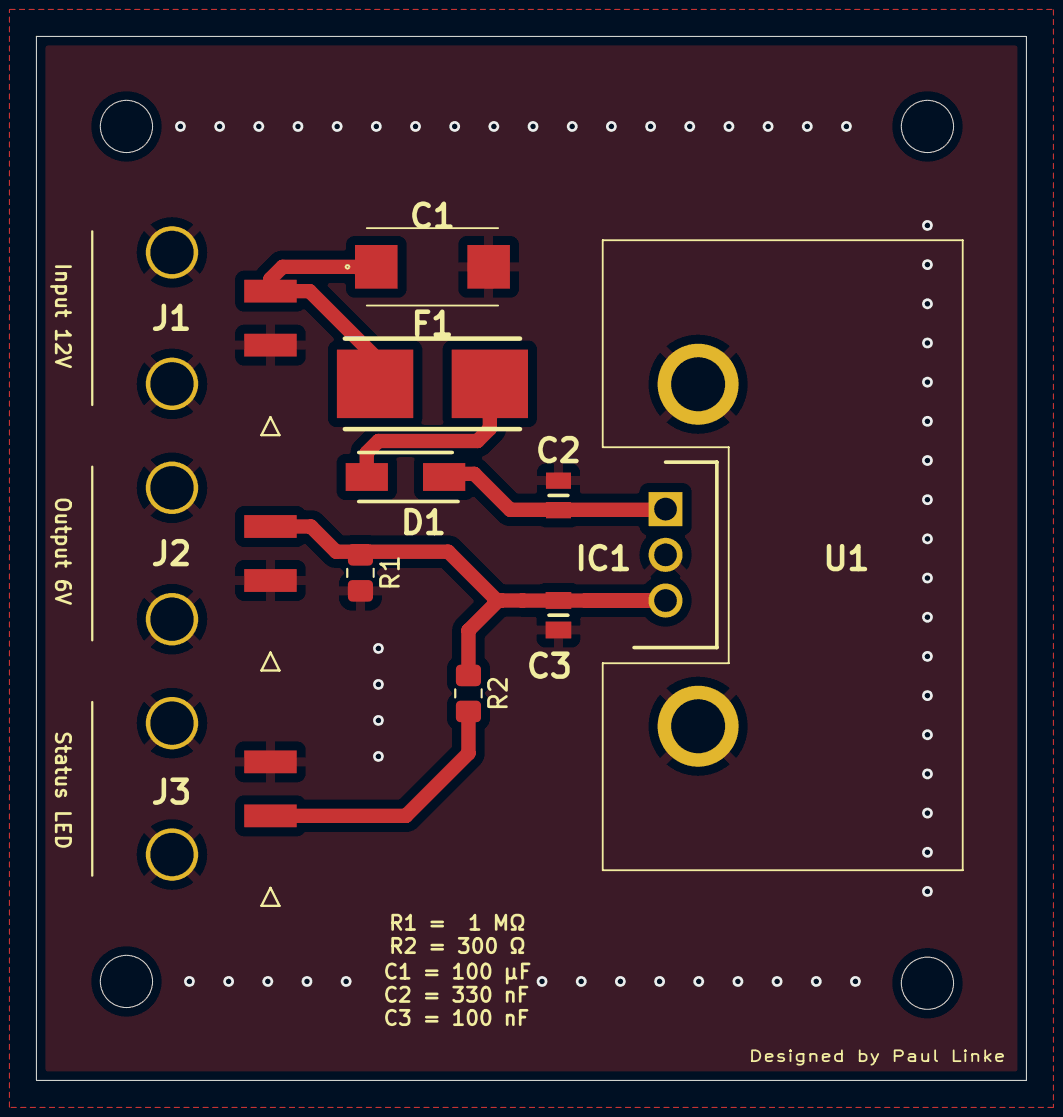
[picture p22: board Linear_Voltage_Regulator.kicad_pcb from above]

Board: 2 copper layers, 55.0 x 58.0 mm, 12 parts (0 on the bottom side), 6 nets.

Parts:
C1: 100 uF; T491X
C2: 330 nF; CAPC2012X100N
C3: 100 nF; CAPC2012X140N
D1: S1M; DIOM5227X270N
F1: 0154001.DRT
IC1: LDO; TO254P460X1010X1720-3P
J1: Input 12V; 43650-02YY_091011
J2: Output 6V; 43650-02YY_091011
J3: Status LED; 43650-02YY_091011
R1: 1 MOhm; R_0805_2012Metric_Pad1.20x1.40mm_HandSolder
R2: 200 Ohm; R_0805_2012Metric_Pad1.20x1.40mm_HandSolder
U1: Heatsink; 513002B02500G

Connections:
GND: C1.2, C2.2, C3.2, IC1.2 (COMMON), J1.1, J1.3, J1.4, J2.1, J2.3, J2.4, J3.2, J3.3, J3.4, R1.2, U1.1, U1.2
unnamed: C1.1, F1.1, J1.2
unnamed: D1.2, F1.2
unnamed: C2.1, D1.1, IC1.1 (INPUT)
unnamed: C3.1, IC1.3 (OUTPUT), J2.2, R1.1, R2.1
unnamed: J3.1, R2.2

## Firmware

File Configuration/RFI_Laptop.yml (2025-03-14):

sweep_points:     1001      # number of points
start_freq:       300e6     # Hz
stop_freq:        6e9       # Hz
res_bw:           3e3       # Hz
vid_bw:           10e3      # Hz
attenuation:      0         # dB 

mode:             HIGH-RES  # Mode of operation: HIGH-RES or FAST
num_aver:         1         # number of traces

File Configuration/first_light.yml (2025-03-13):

sweep_points:     1001      # number of points
start_freq:       500e6     # Hz
stop_freq:        12e9      # Hz
res_bw:           100e3     # Hz
vid_bw:           1e3       # Hz
attenuation:      0         # dB 

mode:             HIGH-RES  # Mode of operation: HIGH-RES or FAST
num_aver:         1         # number of traces

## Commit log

2025-02-27 Initial commit for SPIKES
    [trace_1.csv, trace_2.csv, trace_3.csv, trace_4.csv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]
2025-03-04 update measurements
    [trace_1.csv]
2025-03-04 added shielded enclosure
2025-03-04 added LDO_PSU Doumentation
    [0154001.DRT.stp, 0154001_drt.psm, 43650-0211.stp, 43650-02yy_091011.psm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]
2025-03-04 added LDO_PSU STEP file
    [Voltage_Regulator_for_ZX60-14LN-S+.step]
2025-03-04 added Schematic to Linear Voltage Regulator
    [0154001.DRT.stp, 0154001_drt.psm, 43650-0211.stp, 43650-02yy_091011.psm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]
2025-03-04 fixed schematic
    [Linear_Voltage_Regulator.kicad_sch]
2025-03-04 added Documentation for First Stage
    [0154001.DRT.iam, 0154010.DR.ipt, 43650-0211.iam, 436500211.ipt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]
2025-03-04 added Readme to First Stage
2025-03-04 added step files to first stage
    [First_Stage_Bottom_Print.stp, First_Stage_HexGrill_Print.stp, First_Stage_Top_Print.stp, Regulator_Bracket_Left_Print.stp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]
2025-03-05 fixed sourcing for first stage
    [First_Stage_Sourcing.xlsx]
2025-03-05 added Second Stage Documentation
    [0154001.DRT.iam, 0154010.DR.ipt, 13100151.0005.iam, 13100151.iam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]
2025-03-06 fixed paths
    [trace_1.csv, trace_2.csv]
2025-03-06 first measurement
    [trace_1.csv, trace_2.csv, trace_3.csv, trace_4.csv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]
2025-03-06 new Thursday measurement
    [trace_1.csv, trace_2.csv]
2025-03-06 Deleted Thursday_Test
    [trace_1.csv, trace_2.csv]
2025-03-12 renamed BOMs
    [First_Stage_BOM.xlsx, First_Stage_Sourcing.xlsx, Linear_Voltage_Regulator_BOM.xlsx, Linear_Voltage_Regulator_Sourcing.xlsx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]
2025-03-14 RFI-Laptop Measurement
    [trace_1.csv, trace_2.csv]
2025-04-01 Dphil Student Measurements
    [trace_1.csv, trace_2.csv, trace_3.csv, trace_4.csv]
2025-11-08 naas measurements added
    [trace_1.csv, trace_2.csv]
2025-11-12 naas measurmeents
    [trace_1.csv, trace_2.csv]
2025-11-12 CU Boulder RFI sensor
    [trace_1.csv, trace_2.csv]
2026-06-02 UT-Sensor Measurements
    [trace_1.csv, trace_2.csv, trace_3.csv, trace_4.csv]
2026-06-25 First TART RFI measurement
    [trace_1.csv, trace_2.csv]
